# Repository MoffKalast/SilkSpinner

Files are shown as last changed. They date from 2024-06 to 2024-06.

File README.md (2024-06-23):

# SilkSpinner



An ESP32 powered lab machine for automatic silk cocoons winding. This repository contains the electronics schematic, firmware and 3D printed parts required for full assembly.

The system was designed for the purpose of winding single silkworm cocoons onto sample bobbins for fibre analysis. The current iteration can monitor, drive, and log data for two separate instances at the same time.

The project was developed in cooperation with the Faculty of Natural Sciences and Engineering, University of Ljubljana.

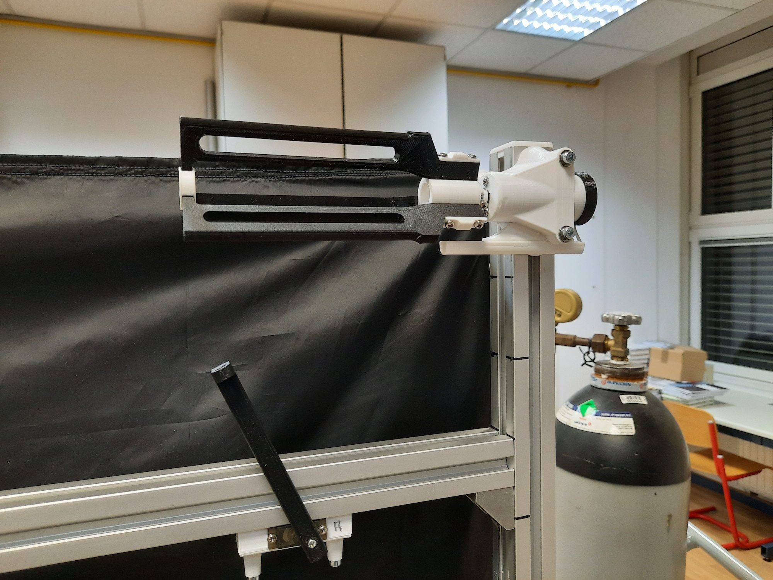
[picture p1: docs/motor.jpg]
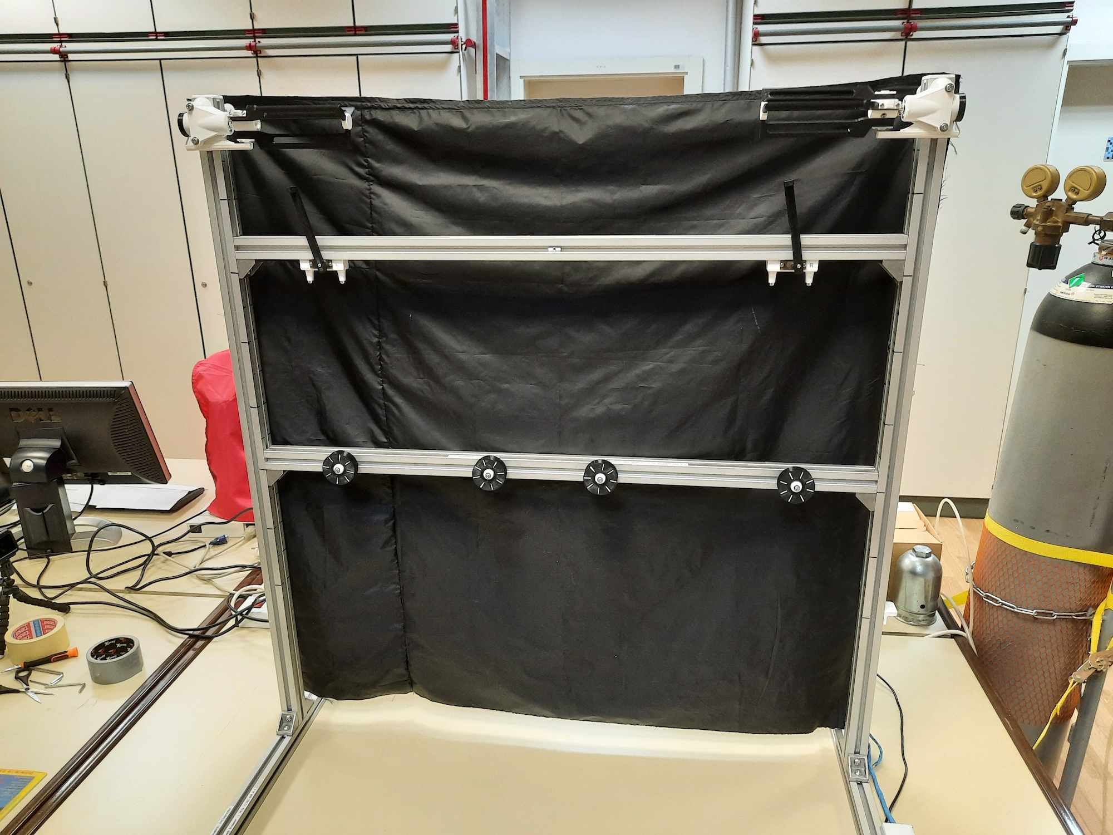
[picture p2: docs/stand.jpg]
|  |   | 
| ----------- | ----------- |
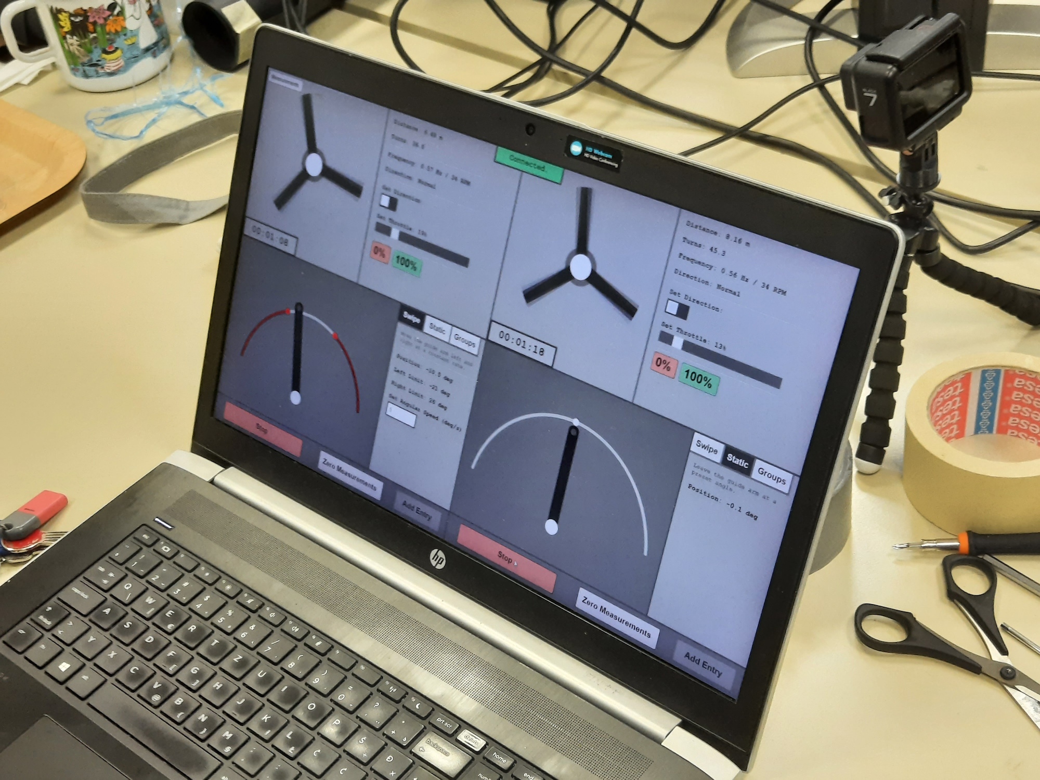
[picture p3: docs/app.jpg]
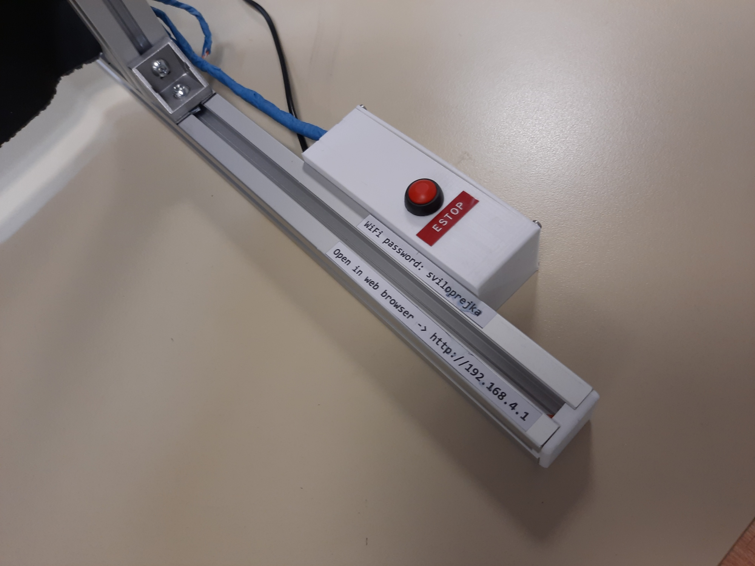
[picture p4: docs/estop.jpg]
|  |  |

## Functonality

The system implements the following functionality:

- guide wheels on bearings to line up and stretch the string

- servo actuators that guide the string onto specific positions of the bobbin, with constant sinusoidal movement that prevents the string from sticking to itself

- automatic sample taking by winding a set distance to a set section of the bobbin (e.g. five samples of 200m, each wound 1 cm apart)

- manual servo control

- smooth start and stop movements for servos and main motors to emulate gentle hand-winding

- adjustable throttle and direction for main motors, speed and angle for actuators

- saving measurement distances and metadata to a `.csv` file and downloading them to the client machine from the web app

- an emergency stop push button, which quickly stops all motors

https://github.com/MoffKalast/SilkSpinner/assets/9977799/55012754-9cc3-48a4-b408-5423bcaef4a0

## Firmware

The ESP firmware is split into two parts: the Arduino control backend and the browser web app that's served from SPIFFS via a WiFi hotspot, both linked together by WebSockets for telemetry and control. 

#### 1. Install Arduino IDE and the following plugins/libraries

- [ESP32](https://randomnerdtutorials.com/installing-the-esp32-board-in-arduino-ide-windows-instructions/)
- [SPIFFS](https://github.com/me-no-dev/arduino-esp32fs-plugin)
- [ESPAsyncWebServer](https://github.com/me-no-dev/ESPAsyncWebServer)
- [AsyncTCP](https://github.com/me-no-dev/AsyncTCP)
- [Arduino_JSON](https://github.com/arduino-libraries/Arduino_JSON)
- [ESP32Servo](https://github.com/madhephaestus/ESP32Servo)

Open `firmware.ino`

#### 2. Write the web app to flash

Running the [ESP32 Sketch Data Upload](https://randomnerdtutorials.com/install-esp32-filesystem-uploader-arduino-ide/) should upload everything in the /data directory that's not part of the main sketch.

#### 3. Build and upload the sketch

As normal, upload the sketch and reset the ESP32. The Wifi hotspot should show up automatically with the default SSID `SilkSpinner` and password `sviloprejka`. The web app can be accessed in a browser at `http://192.168.4.1`

## Electronics

The system runs in an ESP32-WROOM, specifically a devkit V1 wired to the following components as shown on the circuit diagram below:

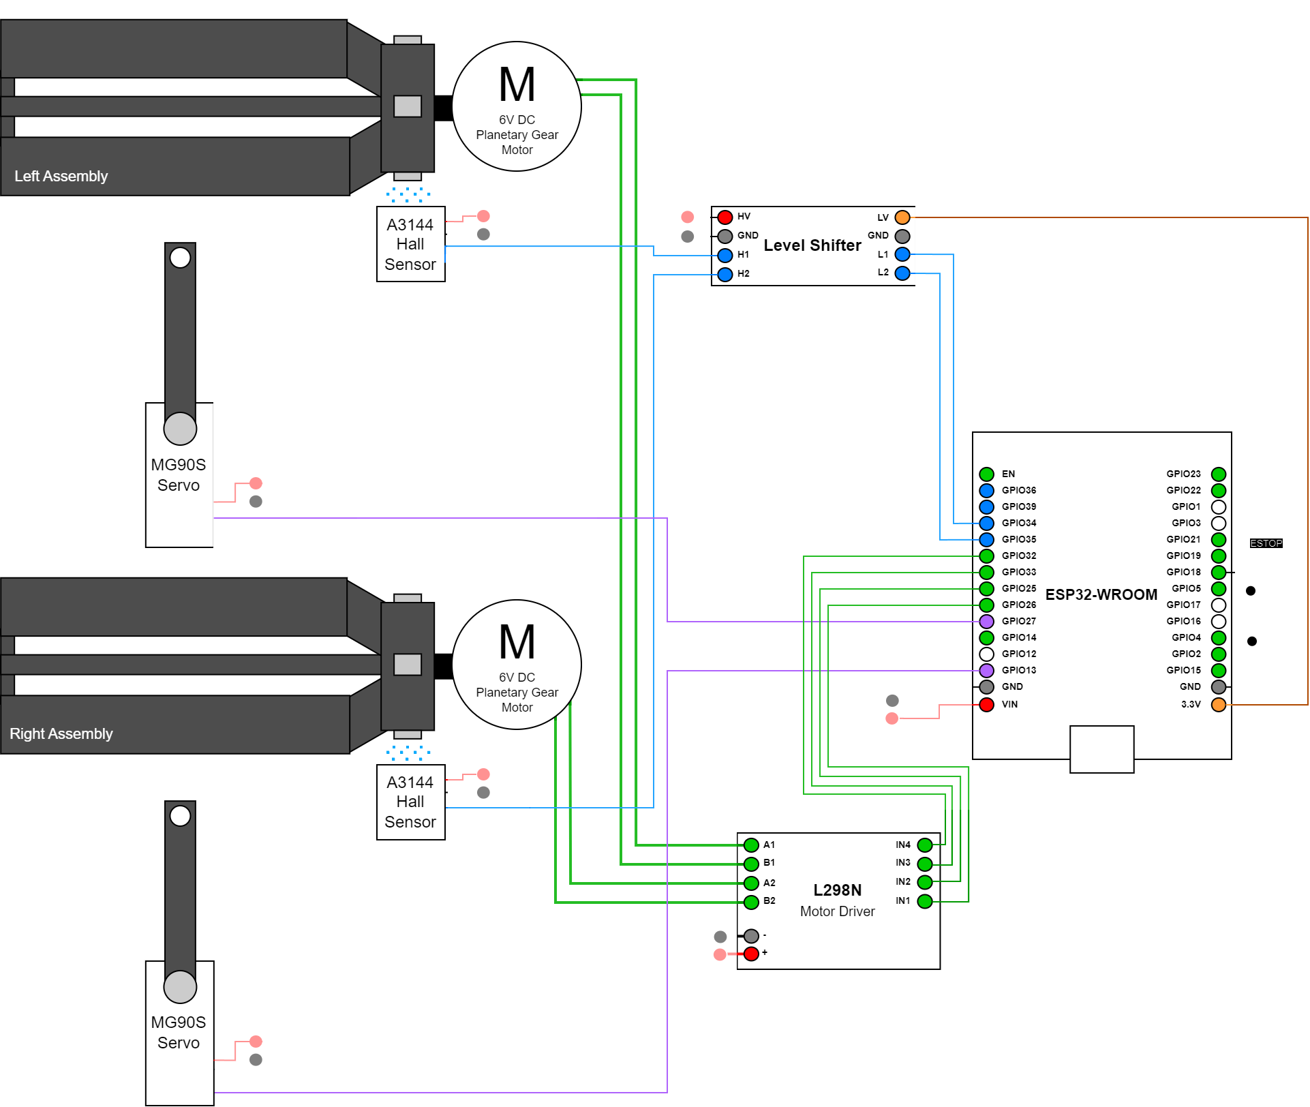
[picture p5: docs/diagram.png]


As the bobbin on each side rotates, the magnets mounted on the central hub pass past the hall sensor and act as an encoder with 3 ticks per rotations, which is used to track the total distance. The level shifters convert the 5V hall sensor signals to safe 3.3V levels.

The following BoM of electronic components was used for the second prototype, most parts are interchangable with general equivallents:

| Quantity | Description                    |  Notes                    |
|----------|--------------------------------|------------------------------------|
| 1        | ESP32-WROOM DevkitV1           | Main MCU                           |
| 1        | L298N Mini                     | Motor driver board                 |
| 1        | BSS138 level shifter           | 3.3 V to 5 V level shifter         |
| 2        | JGA25-370 Geared motor         | Winding motors, 6V, 300 RPM version|
| 2        | A3144 Hall sensor              | Digital hall sensor                |
| 2        | MG90S                          | Director vane micro servo          |
| 1        | 12mm Momentary pushbutton      | ESTOP switch                       |
| a few meters   | Solid strand wire        |                  |

## Mechanical Assembly

The current design uses the following BoM of aluminium extrusions and mounting pieces.

| Quantity | Description                    | Length (mm) | Notes                    |
|----------|--------------------------------|-------------|--------------------------|
| 2        | 30x30 U8 Aluminium Extrusion   | 900         | Cross bars               |
| 2        | 30x30 U8 Aluminium Extrusion   | 1000        | Vertical bars            |
| 2        | 30x30 U8 Aluminium Extrusion   | 600         | Stand                    |
| 8        | 30x30 Right Angle Bracket      | -           | |
| 12       | U8 M4 Mounting Stone           | -           | |
| 12       | M4 L40 Cylindrical Bolt        | -           | |
| 16       | M6 M12 Conical Head Bolt       | -           | |
| 16       | U8 M6 Hammerhead Bolt          | -           | |

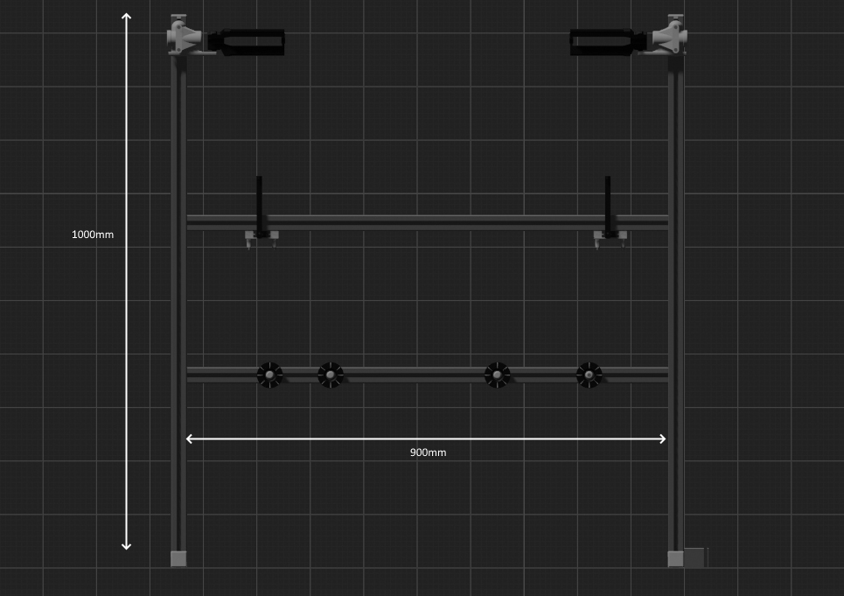
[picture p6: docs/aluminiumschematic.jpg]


The mounting heights for the guide wheel crossbar and servo crossbar are adjustable per-experiment.

The files for the custom 3D printed parts are included in `/3dprint`. Consult the [3D printing readme](3dprint/README.md) for more info.

Other required parts:

| Quantity | Description                    |  Notes                    |
|----------|--------------------------------|------------------------------------|
| 4        | Ball bearing                   | Outer diameter 28mm, inner diameter 12mm               |
| 4        | M3 screws                   | For the electronics box                                  |
| 6        | Neodynium magnet           | 5mm diameter, 3mm height, as the bobbin encoder   |

## Cite

If you're using the Silk Spinner for your research, please cite:

```bibtex
@article{TBD}
``` 

-------------
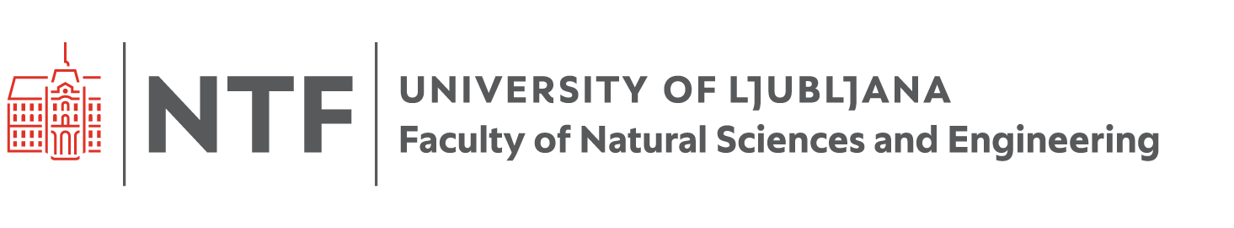
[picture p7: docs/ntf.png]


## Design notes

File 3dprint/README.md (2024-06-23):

## 3D Prints

Consult the `.blend` file for the general layout. 

### ESP32 Enclosure

| Quantity | File Name                   | Description                                                   |
|----------|-----------------------------|---------------------------------------------------------------|
| 1        | electronicsbox.stl          | Main enclosure for housing the electronics.                   |
| 1        | electronicsbox_cover.stl    | Cover for the electronics enclosure.                          |

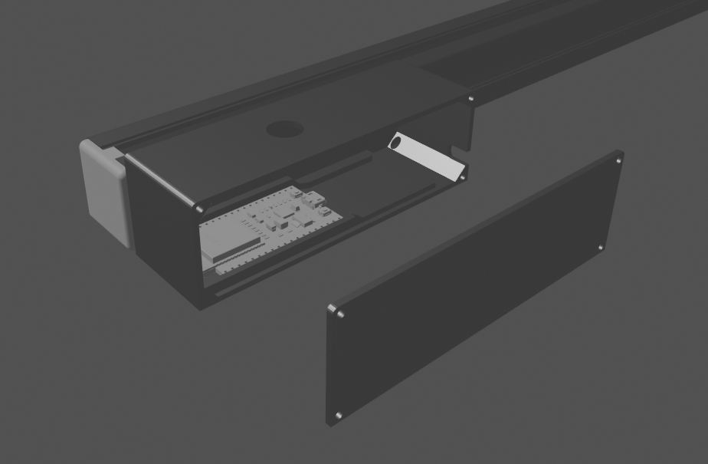
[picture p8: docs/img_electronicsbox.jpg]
 

### Bobbin (2x)

| Quantity | File Name                   | Description                                                   |
|----------|-----------------------------|---------------------------------------------------------------|
| 2        | bobbin_endcap.stl           | End cap to secure the bobbin vanes together.                  |
| 2        | bobbin_hub.stl              | Central hub for mounting the vanes.                           |
| 6        | bobbin_magnetcover.stl      | Covers to hold the magnets to the hub.                        |
| 6        | bobbin_vane.stl             | Three main black vanes.                                       |

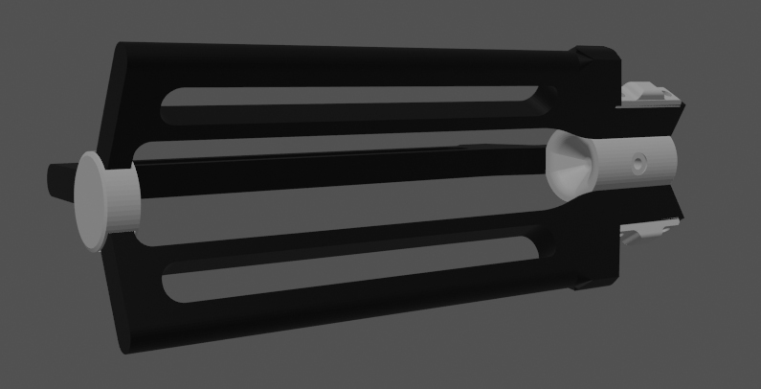
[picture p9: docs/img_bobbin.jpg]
 

### Motor mounts (2x)

| Quantity | File Name                   | Description                                                   |
|----------|-----------------------------|---------------------------------------------------------------|
| 4        | motor_cap.stl               | Motor rear endcap.         |
| 1        | motor_mount_left.stl        | Mounting bracket for the left motor.                          |
| 1        | motor_mount_right.stl       | Mirrored version of the mounting bracket for the right motor.               |
| 2        | motor_sensor_hall_arm.stl   | Arm for mounting the Hall effect sensor on the motor, glue so the hall sensor is directly under the magnet covers.         |

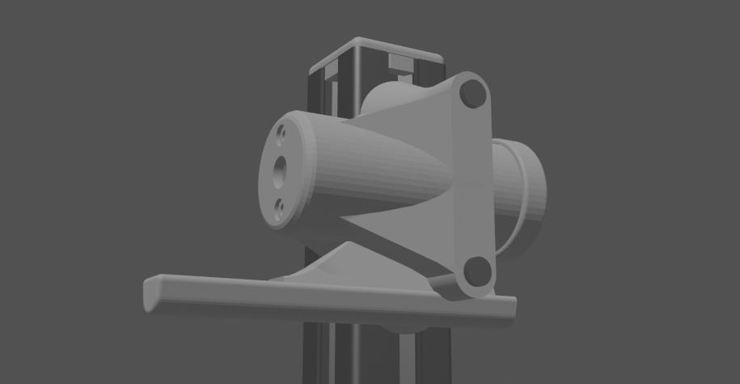
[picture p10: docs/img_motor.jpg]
 

### Servo mounts and arm (2x)

| Quantity | File Name                   | Description                                                   |
|----------|-----------------------------|---------------------------------------------------------------|
| 2        | servo_arm.stl               | Arm for the servo motor which guides the silk thread.             |
| 2        | servo_mount.stl             | Bracket for attaching the servo to the aluminium rails.                         |
| 2        | servo_cover.stl             | Cover for the bracket.                                    |

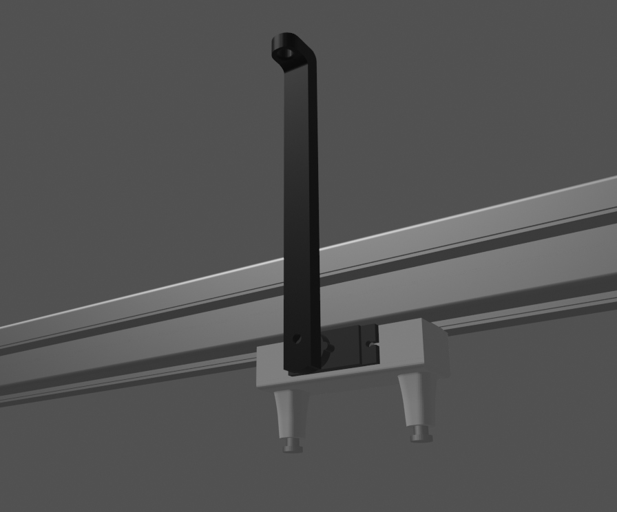
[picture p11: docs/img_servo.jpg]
 

### Guide wheel (4x)

| Quantity | File Name                   | Description                                                   |
|----------|-----------------------------|---------------------------------------------------------------|
| 4        | guidewheel_mount.stl        | Mounting axle for the guide wheel, onto which the bearing mounts.                         |
| 4        | guidewheel.stl              | Guide wheel to align and stretch the silk thread, mount over the bearing.             |
| 4        | guidewheel_cap.stl          | Cap for the guide wheel to screw it in place.                |

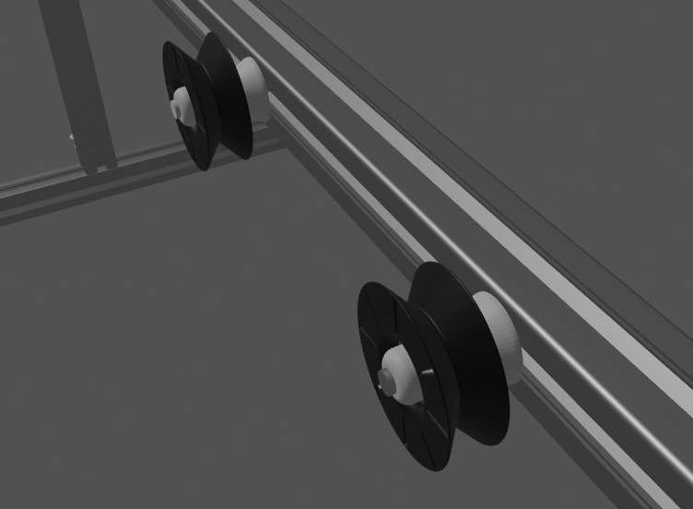
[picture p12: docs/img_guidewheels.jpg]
 

### Misc

| Quantity | File Name                   | Description                                                   |
|----------|-----------------------------|---------------------------------------------------------------|
| 6        | aluminium_endcap.stl        | End cap for aluminium extrusions.                             |
| 1        | tool_holder.stl             | Holder for kex heys required during configuration.            |

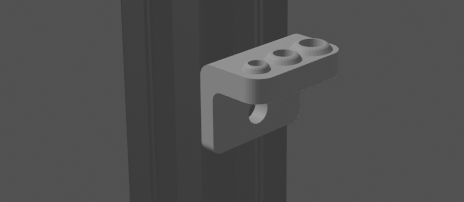
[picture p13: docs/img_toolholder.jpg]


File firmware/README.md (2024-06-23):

## Firmware

### GPIO Assignments

#### Servos
- **Right Servo:** GPIO **13**
- **Left Servo:** GPIO **27**

#### Motors
- **Right Motor 1:** GPIO **25**
- **Right Motor 2:** GPIO **26**
- **Left Motor 1:** GPIO **32**
- **Left Motor 2:** GPIO **33**

#### Hall Sensors
- **Right Hall Sensor:** GPIO **34**
- **Left Hall Sensor:** GPIO **35**

#### Emergency Stop
- **Emergency Stop:** GPIO **18**

## Web App

The application in `/data` consists of several key files:

- `index.html`: Main structure of the web app
- `main.js`: Core functionality and WebSocket communication
- `persistent.js`: Handles data logging and export features
- `modal.js`: Manages modal dialogs
- `style.css`: Styles for the interface

To modify the application, edit these files and update them on the ESP32.

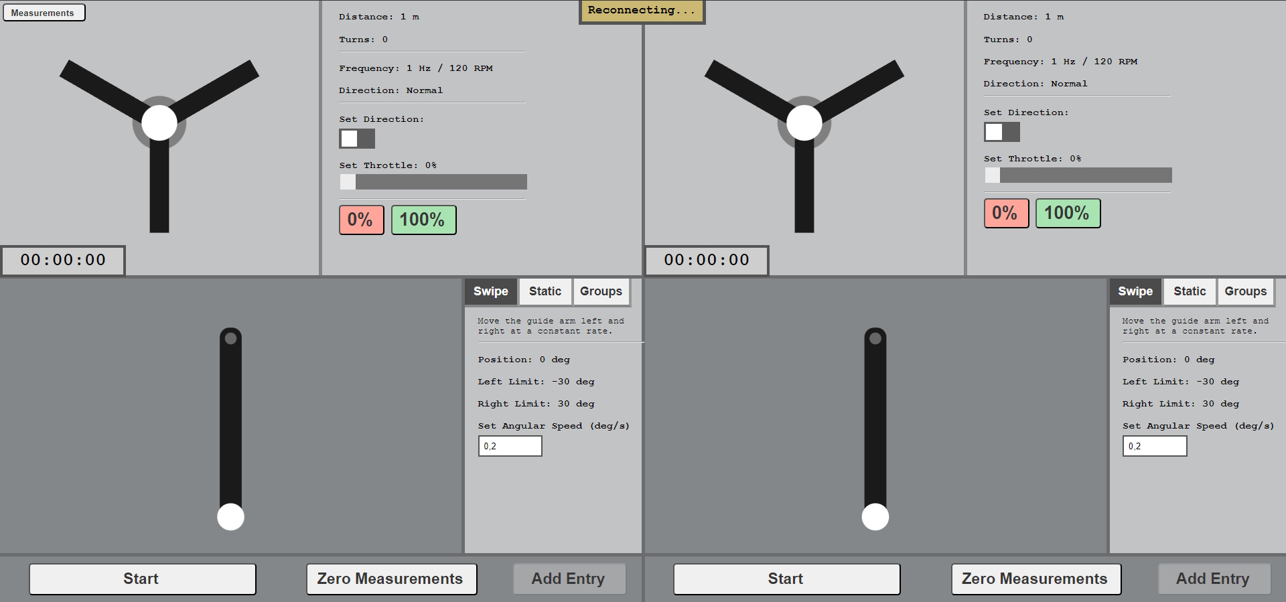
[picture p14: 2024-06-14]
docs/gui.jpg

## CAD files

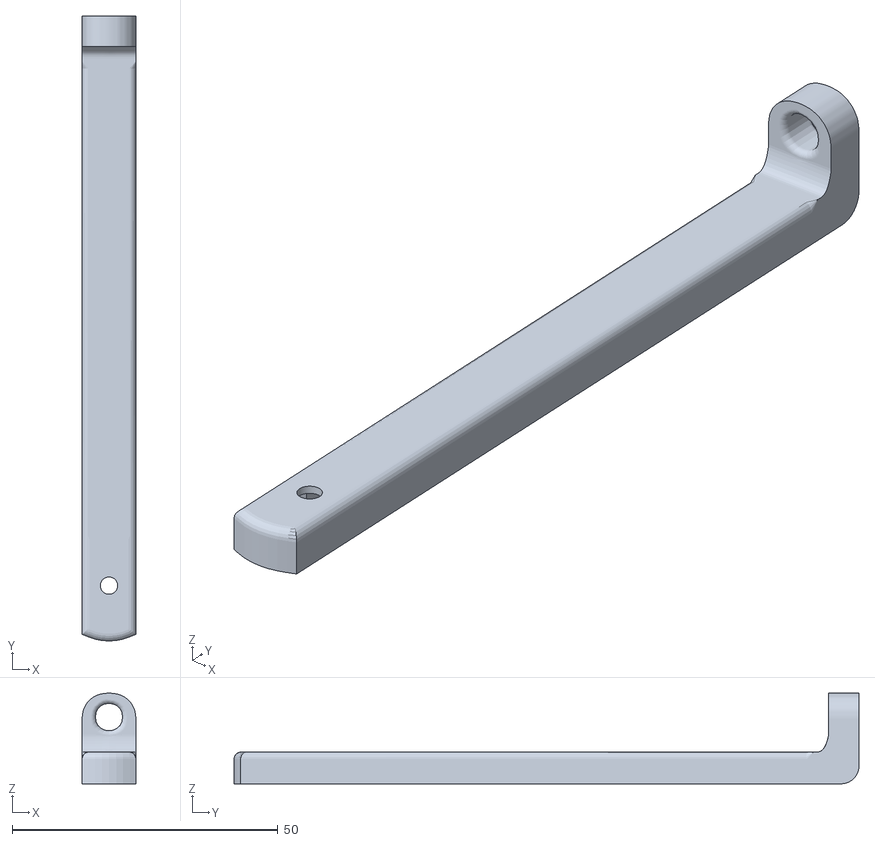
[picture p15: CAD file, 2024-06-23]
3dprint/servo_arm.stl
10.1 x 117.6 x 17.1

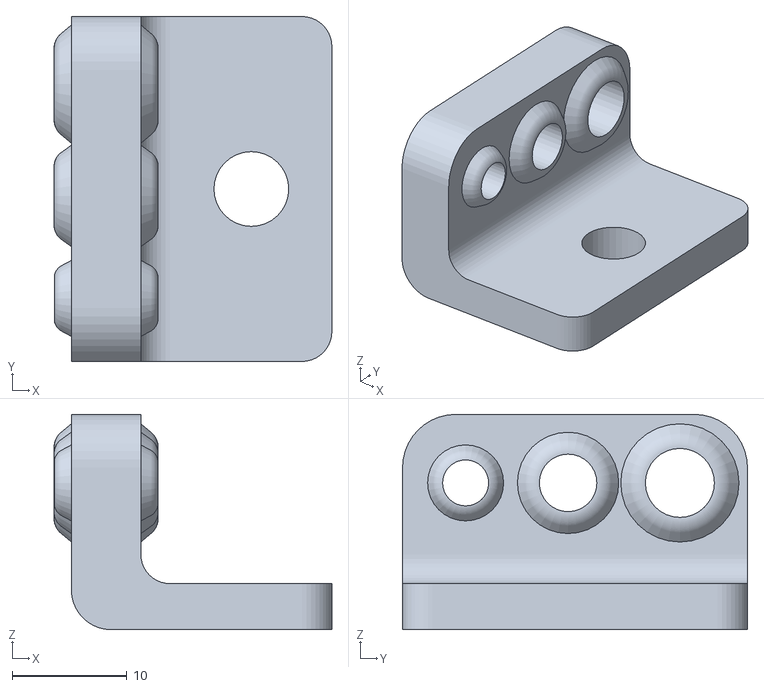
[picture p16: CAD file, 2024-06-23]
3dprint/tool_holder.stl
24.2 x 30.0 x 18.7

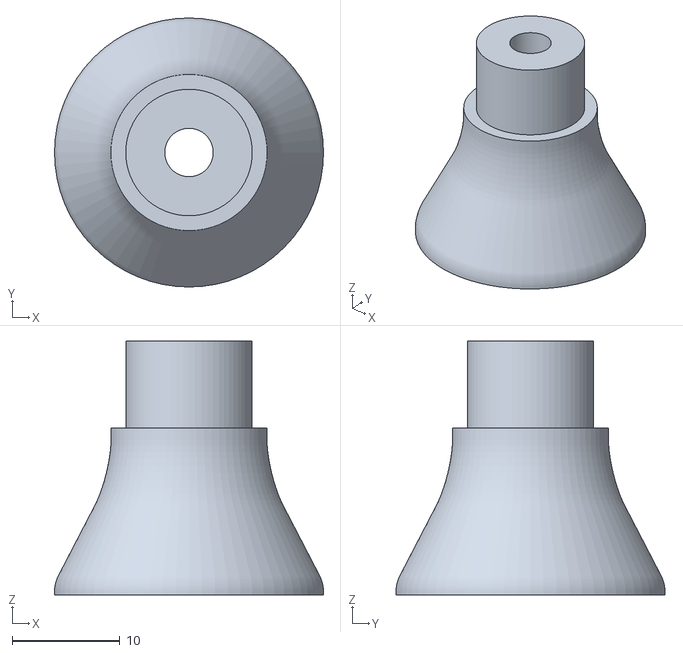
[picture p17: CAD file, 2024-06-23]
3dprint/guidewheel_mount.stl
25.0 x 25.0 x 23.6

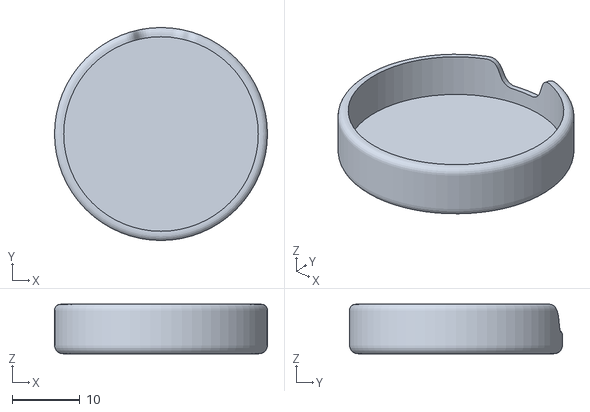
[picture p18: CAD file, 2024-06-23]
3dprint/motor_cap.stl
31.3 x 31.3 x 7.29

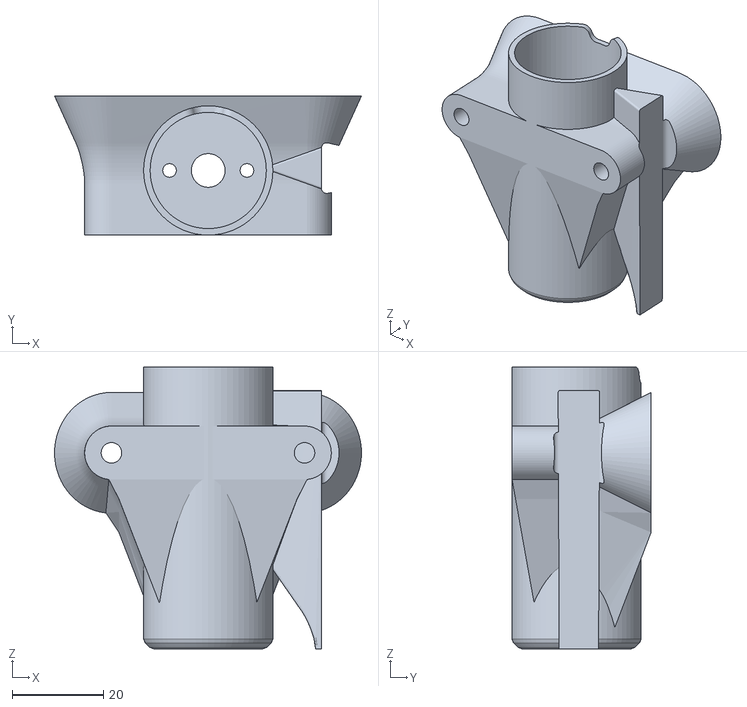
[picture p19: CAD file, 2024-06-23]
3dprint/motor_mount_right.stl
67.4 x 30.6 x 61.8

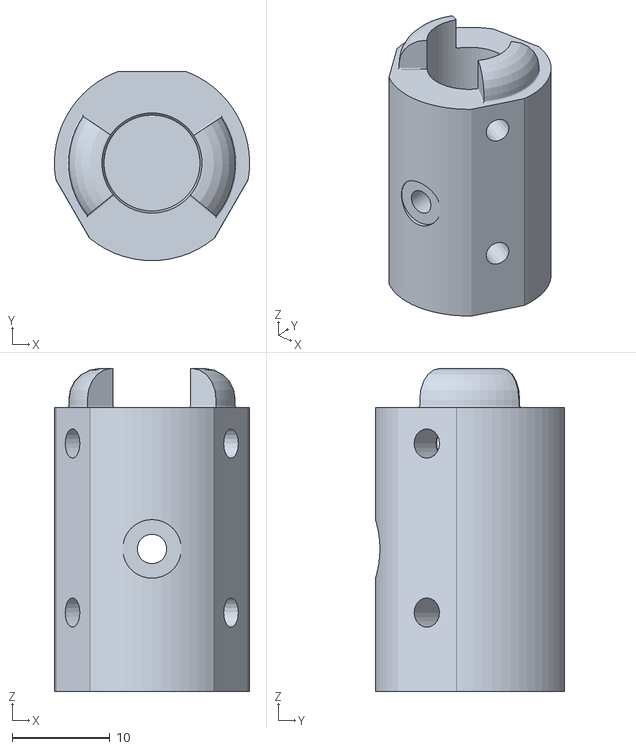
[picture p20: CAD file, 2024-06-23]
3dprint/bobbin_hub.stl
20.0 x 19.4 x 33.1

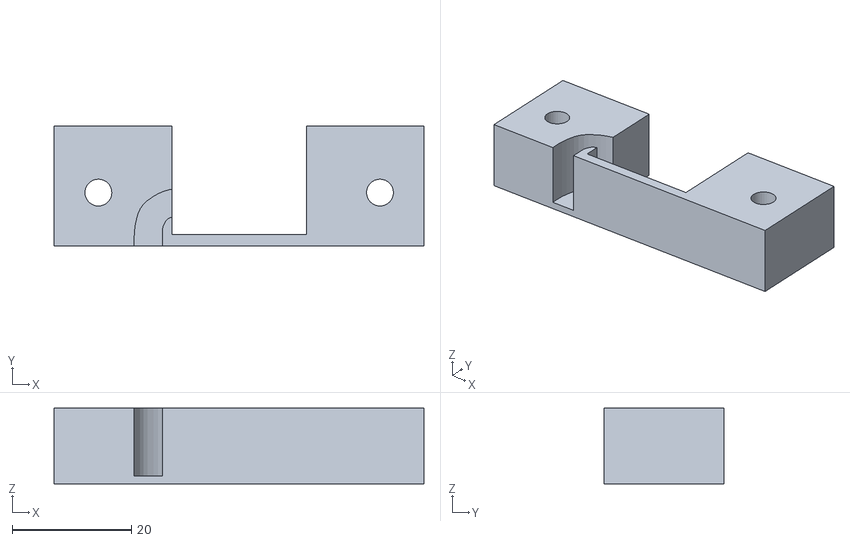
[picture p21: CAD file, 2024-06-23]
3dprint/servo_mount.stl
62.0 x 20.2 x 12.7

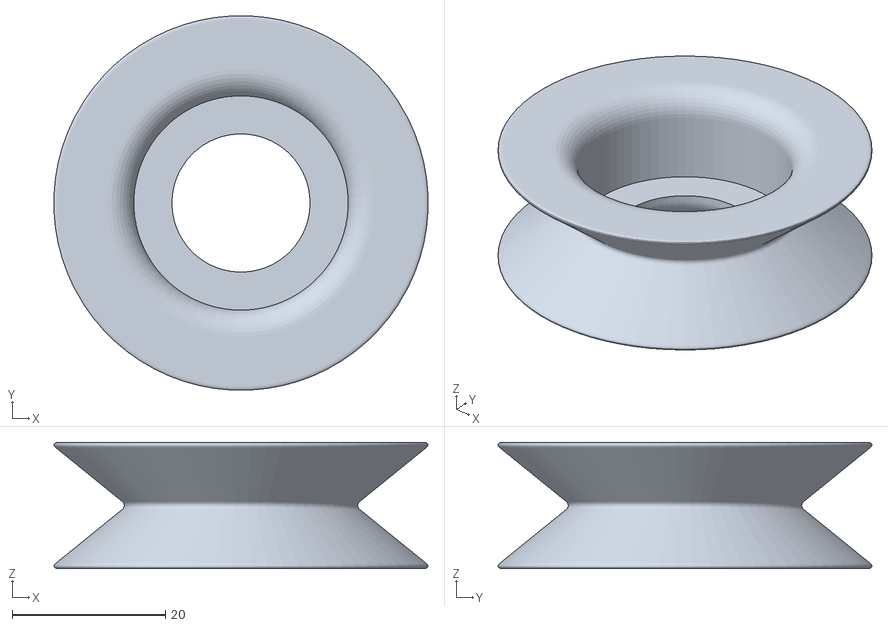
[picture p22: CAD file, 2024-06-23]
3dprint/guidewheel.stl
48.8 x 48.8 x 16.5

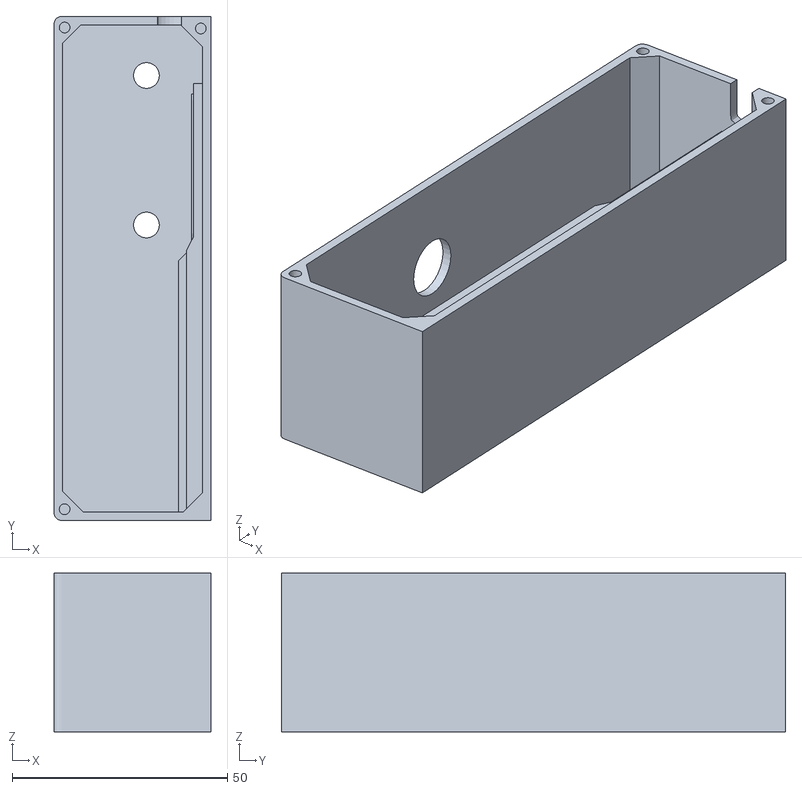
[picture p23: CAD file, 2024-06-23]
3dprint/electronicsbox.stl
36.5 x 117.2 x 37.0

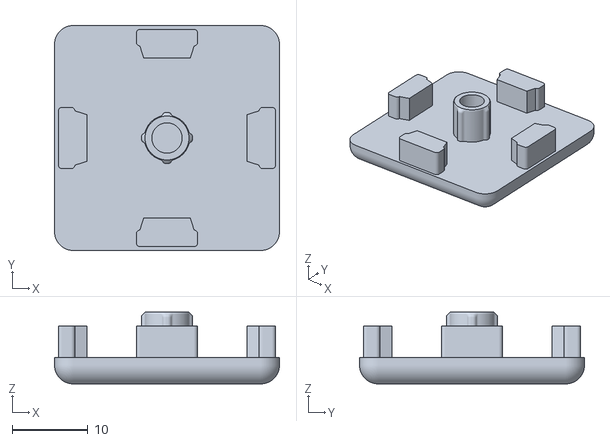
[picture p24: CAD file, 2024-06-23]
3dprint/aluminium_endcap.stl
29.8 x 29.8 x 9.50

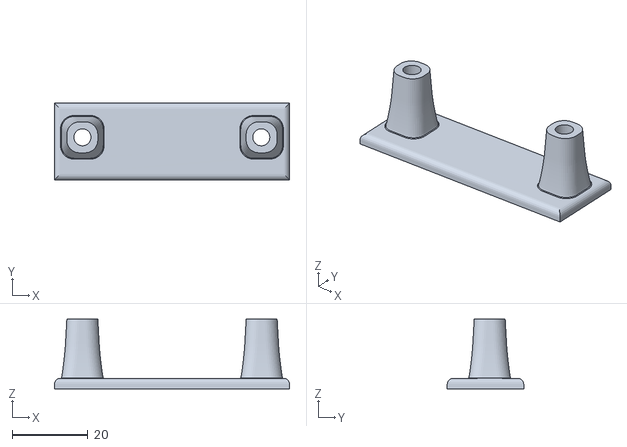
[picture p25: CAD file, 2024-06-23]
3dprint/servo_cover.stl
62.0 x 20.2 x 18.4

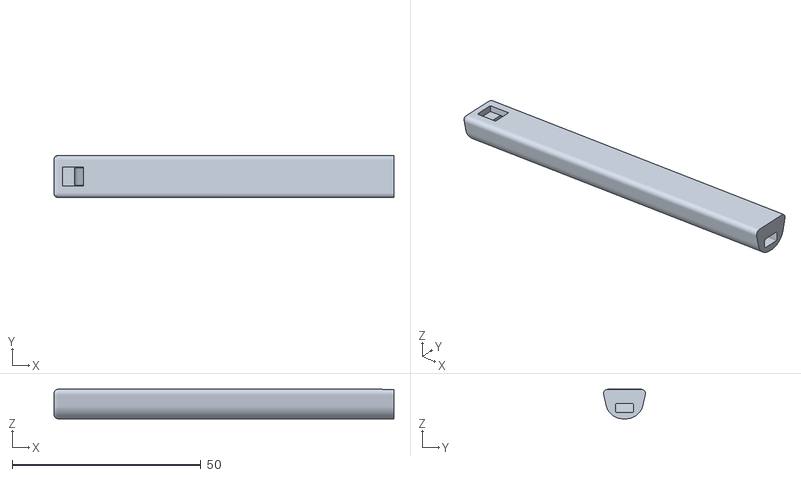
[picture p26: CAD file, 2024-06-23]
3dprint/motor_sensor_hall_arm.stl
90.0 x 11.1 x 7.84

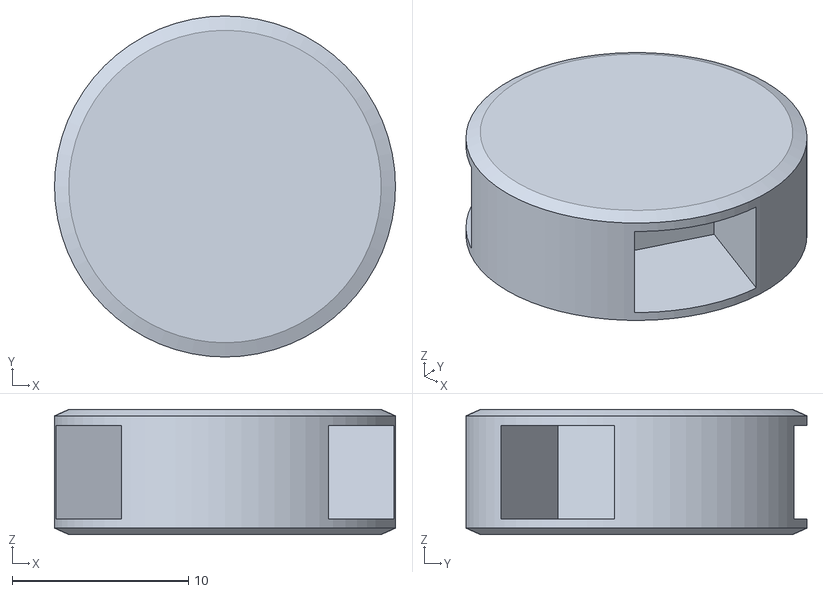
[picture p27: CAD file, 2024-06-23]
3dprint/bobbin_endcap.stl
19.4 x 19.4 x 7.11

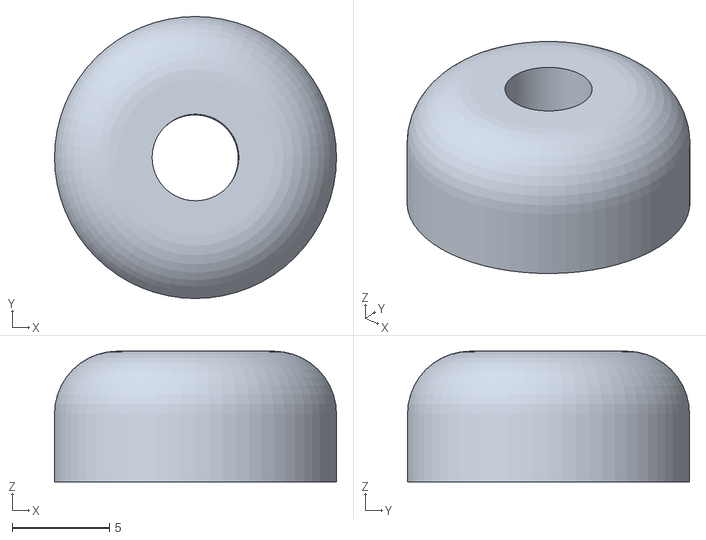
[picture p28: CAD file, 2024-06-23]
3dprint/guidewheel_cap.stl
14.5 x 14.5 x 6.72

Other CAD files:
3dprint/motor_mount_left.stl
3dprint/bobbin_vane.stl
3dprint/bobbin_magnetcover.stl
3dprint/electronicsbox_cover.stl

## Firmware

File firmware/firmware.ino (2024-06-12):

#include "Motor.h"
#include "Servo.h"
#include "Hall.h"
#include "WebApp.h"
#include "Estop.h"

#include <math.h>

#define MODE_SWIPE 0
#define MODE_STATIC 1
#define MODE_GROUPS 2

unsigned long update_time = millis();

extern int counter_left;
extern int counter_right;

extern int L_throttle;
extern int R_throttle;

extern int L_groups;
extern int L_group_len;

extern int R_groups;
extern int R_group_len;

extern bool R_start;
extern bool L_start;

extern int L_angle;
extern int R_angle;

extern int L_angle_min;
extern int L_angle_max;

extern int R_angle_min;
extern int R_angle_max;

extern int L_mode;
extern int R_mode;

extern bool setings_updated;

extern float wiper_state_left;
extern float wiper_state_right;

extern float motor_vel_right;
extern float motor_vel_left;

int L_current_group = 0;
int L_count_zeroer = 0;
float L_group_progress = 0;
bool L_wait_for_servo = true;

int R_current_group = 0;
int R_count_zeroer = 0;
float R_group_progress = 0;
bool R_wait_for_servo = true;

void setup() {
	Serial.begin(115200);

	initMotors();
	initServos();
	initWebApp();
	initESTOP();
}

void updateSockets(){
	if(millis() - update_time > 300){
		sendTelemetry();
		update_time = millis();
		
	}
	else if(setings_updated){
		sendSettingsData();
		setings_updated = false;
	}	
}

int groupSplit(int i, int groups, int minval, int maxval){
	float total = float(maxval - minval);
	float delta = total/(float(groups) - 1.0);

	return round(minval + i*delta);
}

void loop() {

	readSensors();

	if(L_start)
	{
		if(L_mode == MODE_SWIPE){
			updateSwipeLeft();
			setMotorLeft(L_throttle);
		}
		else if(L_mode == MODE_STATIC){
			updateStaticLeft(L_angle);
			setMotorLeft(L_throttle);
		}
		else if(L_mode == MODE_GROUPS){

			if(L_current_group < L_groups)
			{
				if(L_group_progress > L_group_len - 0.06){
					L_current_group++;
					L_group_progress = 0;
					L_count_zeroer = counter_left;
					L_wait_for_servo = true;
					motor_vel_left = 0;
				}
				else{
					L_group_progress = (counter_left-L_count_zeroer) * 0.06;
				}

				int grouploc = groupSplit(L_current_group, L_groups, L_angle_min, L_angle_max);
				if(motor_vel_left == 0.0){
					updateStaticLeft(grouploc);		
				}

				if(L_wait_for_servo){
					setMotorLeft(0);
					if(fabs(float(grouploc)/100.0 - wiper_state_left) < 0.006){
						L_wait_for_servo = false;
					}
				}else if(L_group_progress > L_group_len - 0.5){
					setMotorLeft(L_throttle * 0.15);
				}else if(L_group_progress > L_group_len - 0.2){
					setMotorLeft(L_throttle * 0.03);
				}else{
					setMotorLeft(L_throttle);
				}
			}
			else{
				L_start = false;
				setings_updated = true;
				setMotorLeft(0);
			}
		}
	}
	else
	{
		if(L_mode == MODE_STATIC){
			updateStaticLeft(L_angle);
		}
		setMotorLeft(0);
	}

	if(R_start)
	{
		if(R_mode == MODE_SWIPE){
			updateSwipeRight();
			setMotorRight(R_throttle);
		}
		else if(R_mode == MODE_STATIC){
			updateStaticRight(R_angle);
			setMotorRight(R_throttle);
		}
		else if(R_mode == MODE_GROUPS){

			if(R_current_group < R_groups)
			{
				if(R_group_progress > R_group_len - 0.06){
					R_current_group++;
					R_group_progress = 0;
					R_count_zeroer = counter_right;
					R_wait_for_servo = true;
					motor_vel_right = 0;
				}
				else{
					R_group_progress = (counter_right-R_count_zeroer) * 0.06;
				}

				int grouploc = groupSplit(R_current_group, R_groups, R_angle_min, R_angle_max);
				if(motor_vel_right == 0.0){
					updateStaticRight(grouploc);
				}

				if(R_wait_for_servo){
					setMotorRight(0);
					if(fabs(float(grouploc)/100.0 - wiper_state_right) < 0.006){
						R_wait_for_servo = false;
					}
				}else if(R_group_progress > R_group_len - 0.5){
					setMotorRight(R_throttle * 0.15);
				}else if(R_group_progress > R_group_len - 0.2){
					setMotorRight(R_throttle * 0.03);
				}else{
					setMotorRight(R_throttle);
				}
			}
			else{
				R_start = false;
				setings_updated = true;
				setMotorRight(0);
			}
		}
	}
	else
	{
		if(R_mode == MODE_STATIC){
			updateStaticRight(R_angle);
		}
		setMotorRight(0);
	}

	updateSockets();
	checkESTOP();
}

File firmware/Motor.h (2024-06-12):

#include "driver/ledc.h"

#define PIN_MOTOR1_RIGHT 25
#define PIN_MOTOR2_RIGHT 26

#define PIN_MOTOR1_LEFT 32
#define PIN_MOTOR2_LEFT 33

#define MIN_THROTTLE_LEFT 0.51//0.21//0.7
#define MIN_THROTTLE_RIGHT 0.46//0.18//0.65

#define MAX_THROTTLE 0.92

#define MOTOR_DELTA 0.004
#define MOTOR_DELTA_BRAKE 0.006

extern bool L_dir;
extern bool R_dir;

ledc_channel_config_t ledc_channels[4];

float motor_vel_right = 0.0;
float motor_vel_left = 0.0;

unsigned long update_time_left = millis();
unsigned long update_time_right = millis();

// LEDC_TIMER_1_BIT, 40000000
// LEDC_TIMER_2_BIT, 20000000      
// LEDC_TIMER_3_BIT, 10000000     
// LEDC_TIMER_4_BIT,  5000000    
// LEDC_TIMER_5_BIT,  2500000   
// LEDC_TIMER_6_BIT,  1250000    
// LEDC_TIMER_7_BIT,   625000   
// LEDC_TIMER_8_BIT,   312500  
// LEDC_TIMER_9_BIT,   156250   
// LEDC_TIMER_10_BIT,   78125  
// LEDC_TIMER_11_BIT,   39062  
// LEDC_TIMER_12_BIT,   19531    
// LEDC_TIMER_13_BIT,    9765  
// LEDC_TIMER_14_BIT,    4882 
// LEDC_TIMER_15_BIT,    2441  
// LEDC_TIMER_16_BIT,    1220  
// LEDC_TIMER_17_BIT,     610  
// LEDC_TIMER_18_BIT,     305
// LEDC_TIMER_19_BIT,     152 
// LEDC_TIMER_20_BIT,      76 

void initMotors(){
	pinMode(PIN_MOTOR1_RIGHT, OUTPUT);
	pinMode(PIN_MOTOR2_RIGHT, OUTPUT);
	pinMode(PIN_MOTOR1_LEFT, OUTPUT);
	pinMode(PIN_MOTOR2_LEFT, OUTPUT);

	// configure LEDC timer
	ledc_timer_config_t ledc_timer;
	ledc_timer.speed_mode = LEDC_HIGH_SPEED_MODE;
	ledc_timer.duty_resolution = LEDC_TIMER_12_BIT;
	ledc_timer.timer_num = LEDC_TIMER_3;
	ledc_timer.freq_hz = 19531;
	ledc_timer_config(&ledc_timer);

	ledc_channels[0].channel = LEDC_CHANNEL_4;
	ledc_channels[0].gpio_num = PIN_MOTOR1_RIGHT;

	ledc_channels[1].channel = LEDC_CHANNEL_5;
	ledc_channels[1].gpio_num = PIN_MOTOR2_RIGHT;

	ledc_channels[2].channel = LEDC_CHANNEL_6;
	ledc_channels[2].gpio_num = PIN_MOTOR1_LEFT;

	ledc_channels[3].channel = LEDC_CHANNEL_7;
	ledc_channels[3].gpio_num = PIN_MOTOR2_LEFT;

	for (int i = 0; i < 4; i++) {
		ledc_channels[i].timer_sel = LEDC_TIMER_3;
		ledc_channels[i].duty = 0;
		ledc_channel_config(&ledc_channels[i]);
	}
}

int fix_speed(int mot_speed, float min_throttle){
	if(mot_speed == 0)
		return 0;

	if(mot_speed > 0){
		float offset = min_throttle*100.0 + mot_speed*(1.0 - min_throttle - (1.0 - MAX_THROTTLE));
		if(offset > 100)
			return 100;
		return (int)offset;
	}

	if(mot_speed < 0){
		float offset = -min_throttle*100.0 + mot_speed*(1.0 - min_throttle - (1.0 - MAX_THROTTLE));
		if(offset < -100)
			return -100;
		return (int)offset;	
	}
}

void setPwm(int id, float vel){

	if(vel > MAX_THROTTLE-0.01)
		vel = 1.0;
	else if(vel < -MAX_THROTTLE+0.01)
		vel = -1.0;
	
	ledc_set_duty(LEDC_HIGH_SPEED_MODE, ledc_channels[id].channel, int(abs(vel*4095)));
    ledc_update_duty(LEDC_HIGH_SPEED_MODE, ledc_channels[id].channel);
}

void setMotorLeft(int mot_speed){

	if(millis() - update_time_left < 40){
		return;
	}

	if(L_dir){
		mot_speed = -mot_speed;
	}

	mot_speed = fix_speed(mot_speed, MIN_THROTTLE_LEFT);

	if(mot_speed > 0){
		motor_vel_left = motor_vel_left += MOTOR_DELTA;

		if(motor_vel_left > mot_speed/100.0){
			motor_vel_left = mot_speed/100.0;
		}		
	}else{
		motor_vel_left = motor_vel_left -= MOTOR_DELTA_BRAKE;

		if(motor_vel_left < mot_speed/100.0){
			motor_vel_left = mot_speed/100.0;
		}
	}

	if(motor_vel_left > -MIN_THROTTLE_LEFT && motor_vel_left < MIN_THROTTLE_LEFT){
		if(mot_speed > 0){
			motor_vel_left = MIN_THROTTLE_LEFT;
		}
		else if(mot_speed < 0){
			motor_vel_left = -MIN_THROTTLE_LEFT;
		}
		else{
			motor_vel_left = 0;
		}
	}
	
	if(motor_vel_left < 0){
		setPwm(0,motor_vel_left);
		setPwm(1,0);
	}else{
		setPwm(0,0);
		setPwm(1,motor_vel_left);
	}
	

	update_time_left = millis();
}

void setMotorRight(int mot_speed){

	if(millis() - update_time_right < 40){
		return;
	}

	if(R_dir){
		mot_speed = -mot_speed;
	}

	mot_speed = fix_speed(mot_speed, MIN_THROTTLE_RIGHT);

	if(mot_speed > 0){
		motor_vel_right = motor_vel_right += MOTOR_DELTA;

		if(motor_vel_right > mot_speed/100.0){
			motor_vel_right = mot_speed/100.0;
		}		
	}else{
		motor_vel_right = motor_vel_right -= MOTOR_DELTA;

		if(motor_vel_right < mot_speed/100.0){
			motor_vel_right = mot_speed/100.0;
		}
	}

	if(motor_vel_right > -MIN_THROTTLE_RIGHT && motor_vel_right < MIN_THROTTLE_RIGHT){
		if(mot_speed > 0){
			motor_vel_right = MIN_THROTTLE_RIGHT;
		}
		else if(mot_speed < 0){
			motor_vel_right = -MIN_THROTTLE_RIGHT;
		}
		else{
			motor_vel_right = 0;
		}
	}

	if(motor_vel_right < 0){
		setPwm(2,0);
		setPwm(3,motor_vel_right);
	}else{
		setPwm(2,motor_vel_right);
		setPwm(3,0);
	}

	update_time_right = millis();
}

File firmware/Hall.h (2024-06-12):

#define PIN_HALL_RIGHT 34
#define PIN_HALL_LEFT 35

#define SIG_HIGH 1700
#define SIG_LOW 1200

#define DEBOUNCE_MS 140

int counter_left = 0;
int counter_right = 0;

float frequency_right = 0;
float frequency_left = 0;

unsigned long prev_spin_time_left = millis();
unsigned long spin_time_left = millis();

unsigned long prev_spin_time_right = millis();
unsigned long spin_time_right = millis();

int prev_counter_left = 0;
int prev_counter_right = 0;

unsigned long update_time_hall = millis();

int state_left = 0;
int state_right = 0;

int getMagnetState(int rawmagnet){
	if(rawmagnet < SIG_LOW)
		return 0;
	if(rawmagnet > SIG_HIGH)
		return 2;
	return 1;
}

// val 0 low, 1 mid, 2 high
int stateMachine(int state, int rawmagnet){

	if(state > 9)
		return state;
	
    const int transitions[][2] = {
        {1, 2},
        {2, 2},
        {3, 2},
        {4, 2},
        {5, 2},
        {6, 1},
        {7, 1},
        {8, 0},
        {9, 0},
        {10, 0}
    };

    int match = transitions[state][1];

    if(getMagnetState(rawmagnet) == match)	
    	return transitions[state][0];
    	
    return state;
}

void readSensors(){
	if(millis() - update_time_hall < 2){
		return;
	}

	state_left = stateMachine(state_left, analogRead(PIN_HALL_LEFT));
	if(state_left == 10 ){

		if(millis() - spin_time_left > DEBOUNCE_MS){
			counter_left++;

			prev_spin_time_left = spin_time_left;
			spin_time_left = millis();	

			frequency_left = 333.3333/float(spin_time_left - prev_spin_time_left);
		}
		
		state_left = 0;
	}

	state_right = stateMachine(state_right, analogRead(PIN_HALL_RIGHT));
	if(state_right == 10){

		if(millis() - spin_time_right > DEBOUNCE_MS){
			counter_right++;
	
			prev_spin_time_right = spin_time_right;
			spin_time_right = millis();

			frequency_right = 333.3333/float(spin_time_right - prev_spin_time_right);
		}
		
		state_right = 0;
	}

	update_time_hall = millis();
}

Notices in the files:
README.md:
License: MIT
